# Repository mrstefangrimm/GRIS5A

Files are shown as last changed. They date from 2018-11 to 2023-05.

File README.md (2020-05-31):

# Marker Motion X-Ray Imaging Phantom
GRIS5A (working title) is a motion phantom with 5 motion axes which are controlled independently for both linear and rotary motion.
The name "Gris" "5A" comes from its color (gray) and the 5 axes. 

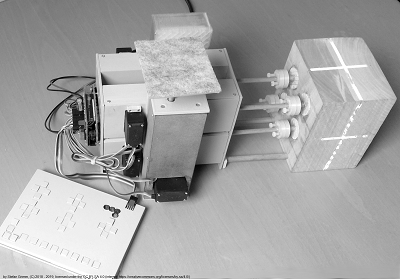
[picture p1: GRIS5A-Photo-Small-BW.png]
No2 Motion Phantom


## Project History
The project was launched in 2017 and has been added to github in 2018. In 2020, the software that is shared with other projects has been moved to its own repository named Phaso.

## Construction

A detailed description how to build this phantom is published on *[Instructables.com](https://www.instructables.com/id/Marker-Motion-X-Ray-Imaging-Phantom/)*.

## Manufacturing Tool Chain

### Mechanical Design

Tool | License 
---- | -------
SketchUp | SketchUp Shop 
Ultimaker Cura | GPL

### Hardware Design

Tool | License 
---- | -------
Fritzing | GPL

## License



This work is licensed under the Creative Commons Attribution-ShareAlike 4.0 International License. To view a copy of this license, visit http://creativecommons.org/licenses/by-sa/4.0/ or send a letter to Creative Commons, PO Box 1866, Mountain View, CA 94042, USA.

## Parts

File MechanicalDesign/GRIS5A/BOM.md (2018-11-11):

Anz. | Beschreibung
---- | ------------ 
2 | Holz Rundprofil d8 x 175
16 | M2 x 10 Universal Senkkopfschrauben mit S-Spitze
4 | M2 x 16 Universal Senkkopfschrauben mit S-Spitze
3 | LnR Actuator in linker Ausführung
2 | LnR Actuator in rechter Ausführung
1 | DKb Platine bestückt
1 | 8 pin Kabel
2 | 8 pin Stecker
1 | DKb-Front
1 | DKb-Back
1 | Niederstromnetzteil 230V/12V 0.7 A
1 | Niederstromnetzteil 230V/5V 2 A
1 | Stromkabel 2 phasig d0.4 x 200 für das Servoshield
1 | Stromkabel 2 phasig d0.4 x 200 mit Stecker d5.5/2.1 für den Arudino
1 | Stromkabel 2 phasig für den 230V Anschluss
1 | Gris5A-NetzteilGrundplatte
1 | Gris5A-NetzteilDeckel
1 | Arduino Uno R3
1 | Adafruit Servoshield PWM16
1 | Gris5A-Front
1 | Gris5A-Back
4 | Gris5A-Flansch
4 | Gris5A-FlanschHalter
2 | Gris5A-PhantomKlammer
1 | Gris5A-GatingGrundplatte
1 | Gris5A-GatingPlattform
1 | Gris5A-GatingBodenplatte
1 | Gris5A-GatingDeckplatte

<br />This work is licensed under a <a rel="license" href="http://creativecommons.org/licenses/by-sa/4.0/">Creative Commons Attribution-ShareAlike 4.0 International License</a>.

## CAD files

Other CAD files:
MechanicalDesign/Common/SketchUp/Cmn-Flange.skp
MechanicalDesign/Common/SketchUp/Cmn-FlangeClip.skp
MechanicalDesign/Common/SketchUp/Cmn-FrontClip.skp
MechanicalDesign/Common/SketchUp/Cmn-GatingPlatform.skp
MechanicalDesign/GRIS5A/SketchUp/DKb-Back.skp
MechanicalDesign/GRIS5A/SketchUp/DKb-Front.skp
MechanicalDesign/GRIS5A/SketchUp/Gris5A-Body.skp
MechanicalDesign/GRIS5A/SketchUp/Gris5A-BodyExplosion.skp
MechanicalDesign/GRIS5A/SketchUp/Gris5A-BodyRigidMarkers.skp
MechanicalDesign/GRIS5A/SketchUp/Gris5A-CylindersExplosion.skp
MechanicalDesign/GRIS5A/SketchUp/Gris5A-Flansch.skp
MechanicalDesign/GRIS5A/SketchUp/Gris5A-FlanschHalter.skp
MechanicalDesign/GRIS5A/SketchUp/Gris5A-FrontPlatte.skp
MechanicalDesign/GRIS5A/SketchUp/Gris5A-GatingBodenplatte.skp
MechanicalDesign/GRIS5A/SketchUp/Gris5A-GatingDeckplatte.skp
MechanicalDesign/GRIS5A/SketchUp/Gris5A-GatingGrundplatte.skp
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

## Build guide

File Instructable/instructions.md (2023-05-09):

# Marker Motion X-Ray Imaging Phantom

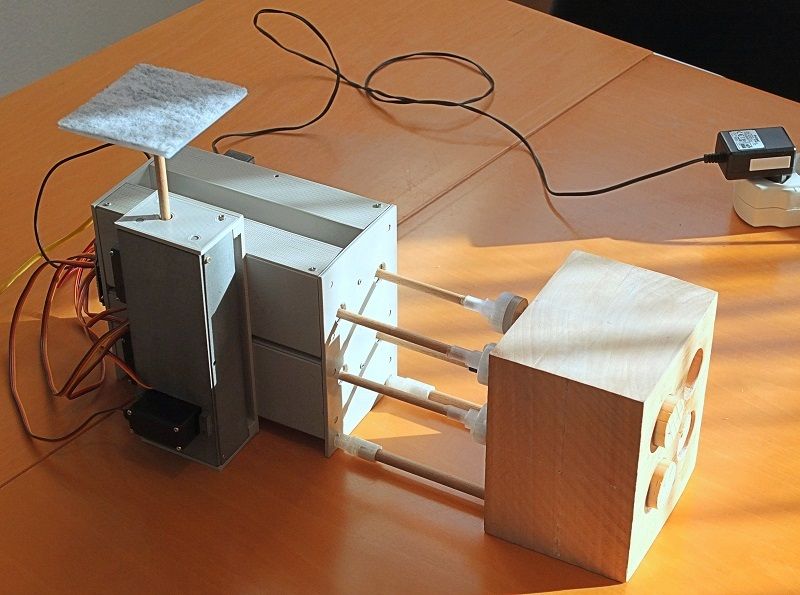
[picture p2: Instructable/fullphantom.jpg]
fullphantom


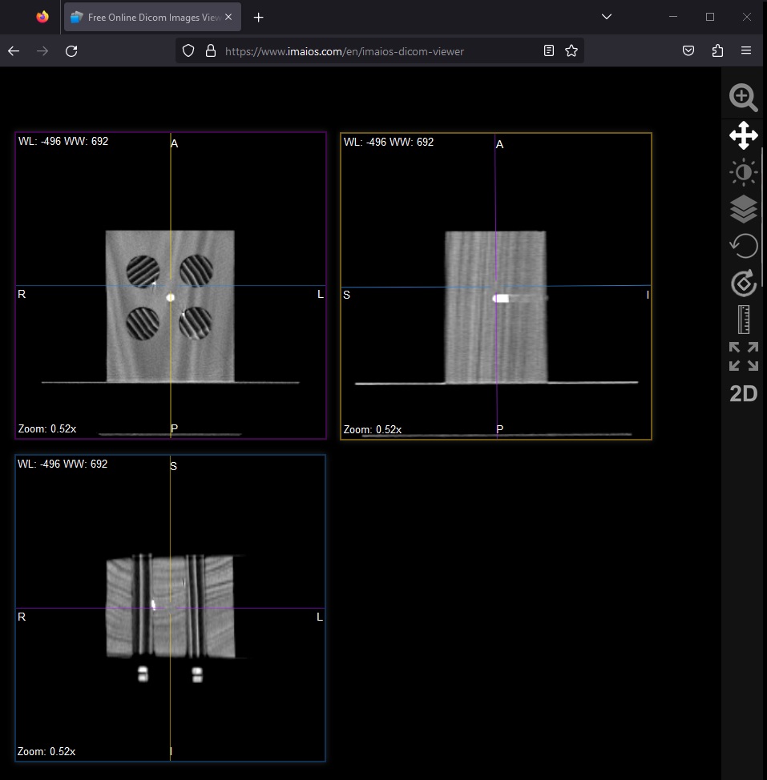
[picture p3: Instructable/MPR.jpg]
MPR


https://youtu.be/TMkLDR-dig4
https://youtu.be/PLr7lDx5VoA
https://youtu.be/z_6X1krTg_E

In the field of medical imaging, so called imaging phantoms are used  to evaluate, analyze, and tune the performance of various imaging  devices (Source: Wikipedia). 

Markers, or fiducial markers, are small, highly visible objects implanted in the patient’s body and used as “landmarks”.  Markers are implanted in  organs like the liver, the prostate, the pancreas or even the lung.  Markers in medical imaging are used to correlate images or to track  motion. This specially developed imaging  phantom simulates marker motion based on respiratory motion.

The idea for this phantom came when I studied marker motion. In a prostate, markers are implanted to correlate images. The markers do  not move during the image acquisition unless the patient moves. It is  possible that the markers slowly move over days which leads to different topologies. Markers in a liver move up and down with the respiratory  motion. Markers in the liver move as a group whereas in the lung, marker may move in different directions when the patient breathes.

On an X-Ray image, the material and the density define what is a  bone, a liver or a lung. Wood for example is similar to a lung. The four freely movable cylinders are made of wood and are used to simulate motion of the markers. The metal markers have a much higher density (> 10000 times higher) than wood and are clearly visible on an X-Ray image.

This short animation demonstrates some motion patterns of the Marker Motion X-Ray Imaging Phantom in simulation and reality:
https://youtu.be/S2i1PQueZQw

To generate the motion, the phantom uses five [LnR-Actuators](https://www.instructables.com/id/Linear-and-Rotation-Actuator/), an Arduino micro controller and an Adafruit Servo Shield. The phantom can be remote controlled from a Windows PC or Android Device over an USB cable.

This phantom is suitable to evaluate and tune the performance of medical devices. A field of application could be the development of motion tracking and marker detection and matching algorithms. With the used materials, imaging dosimetry is not possible. 

The direct material costs are approximately USD 250.

### Supplies:

1 Arduino Uno

1 Adafruit 16-Channel Servo Shield

5 [LnR-Actuator](https://www.instructables.com/id/Linear-and-Rotation-Actuator/)

4 Metal marker d1 x l4 mm, created from paper clip

9 Screw M2 x l10

4 Screw M2 x l20

1 Wooden block l100 x w120 x h180 mm

4 Wooden cylinders  d30 x l100 mm

4 Wooden dowel d6 x l25 mm

1 Wooden dowel d6 x l42 mm

2 Wooden dowel d8 x l166 mm

2 Wooden dowel d8 x l110 mm

3 Graphite lead of a pencil d2 x l12 mm

8 Graphite lead of a pencil d2 x l5 mm

1 Windows PC with Java 8 runtime and .NET Framework 4.6.2

1 3D Printer

1 Standing drill and drills for wood: d30, d8, d6 and d2 mm

Legend: l:length, d:diameter, w: width, h:height

## Step 1: 3D Printed Parts

PLA, default 20% infill: Cmn-FlangeClip.stl, Cmn-FrontClip.stl, Cmn-GatingPlatform.stl, MMXIP-Back.stl, MMXIP-Flange.stl, MMXIP-FlangeCylinder.stl, MMXIP-Front.stl, MMXIP-GatingBase.stl, MMXIP-GatingBottom.stl, MMXIP-GatingTop.stl

## Step 2: Build the Phantom Body

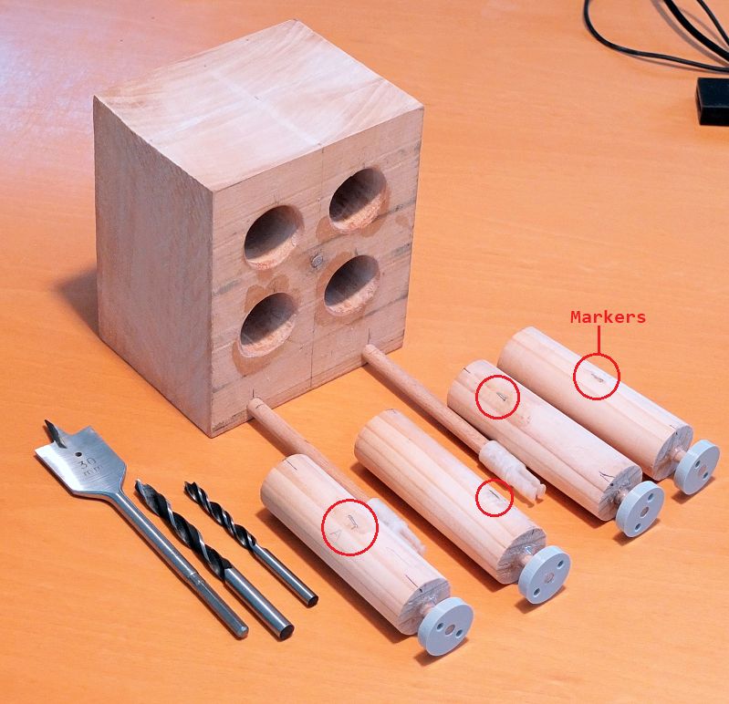
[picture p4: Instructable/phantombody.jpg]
phantombody

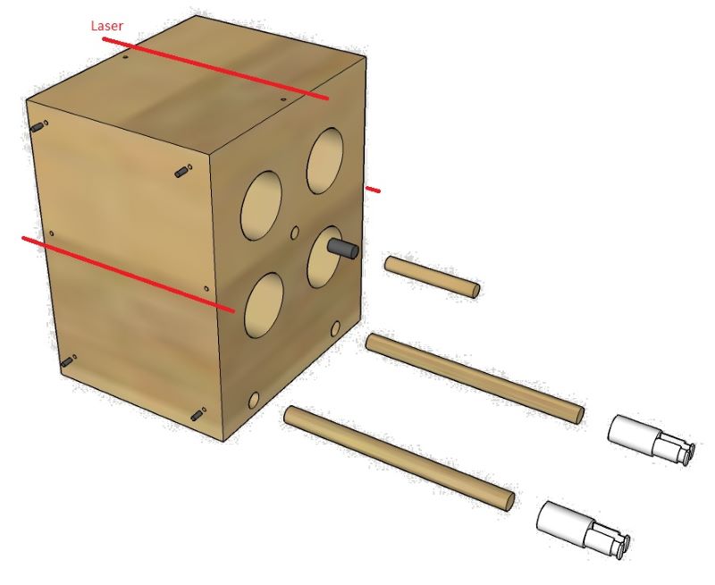
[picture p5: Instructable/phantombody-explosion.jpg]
phantombody

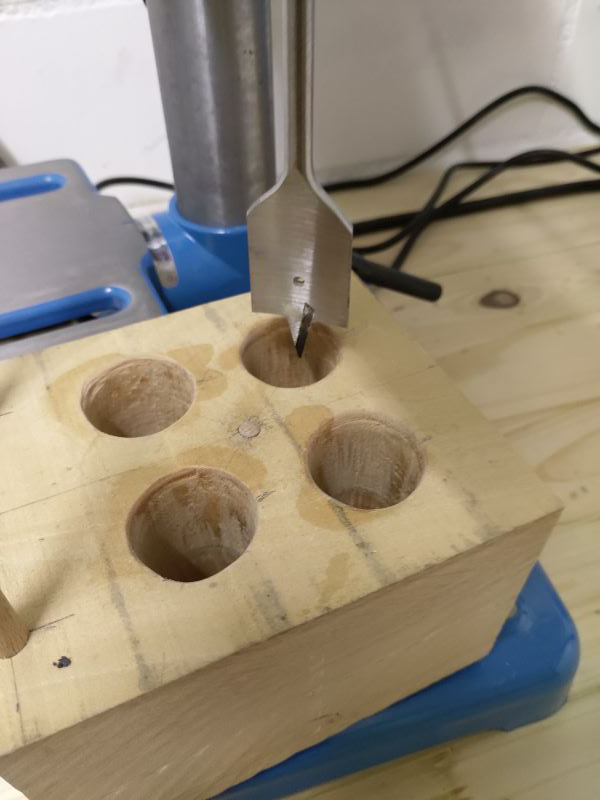
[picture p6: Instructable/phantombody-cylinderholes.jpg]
phantombody

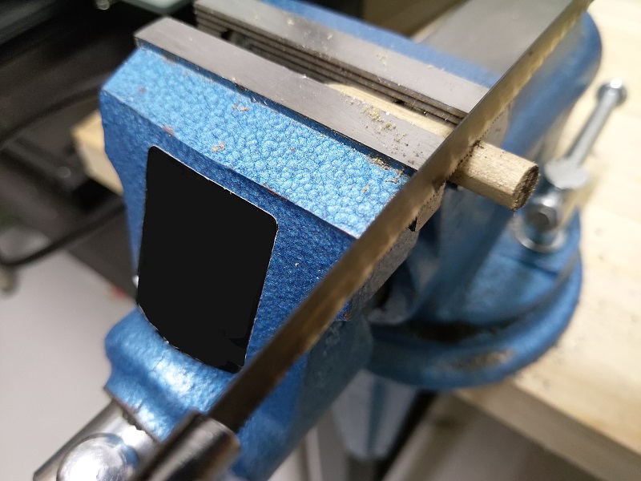
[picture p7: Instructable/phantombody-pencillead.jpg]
phantombody

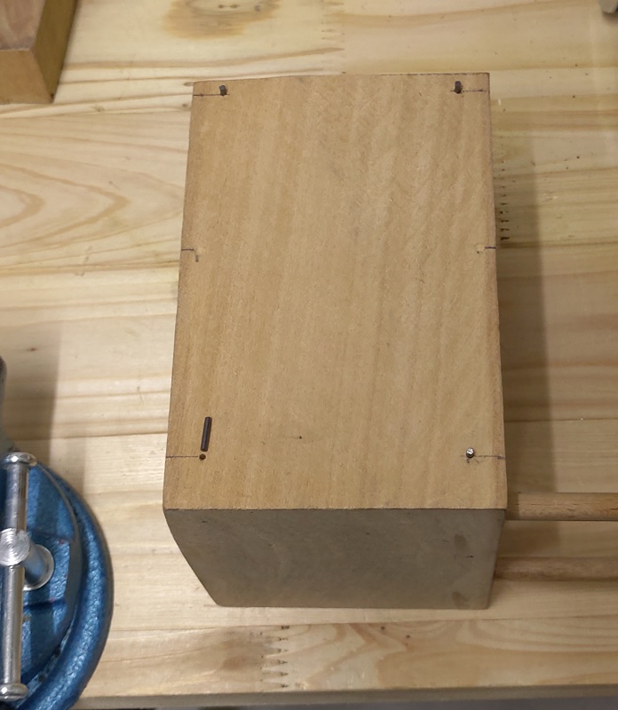
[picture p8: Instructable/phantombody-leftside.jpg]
phantombody


The "phantom body" is the wooden cube as seen in the images above. It has 4 bores that allow the cylinders to rotate and move back and forth. In the center of the four cylinder bores is a 6 mm hole filled with graphite from a pencil lead (this is clearly visible on an x-ray and represents the target).

Markings on the sides and top of the phantom help align the phantom with the laser. On the left and right side are four pins made from a pencil lead as rigid markers visible on x-rays.

First, use a pencil to mark where you need to drill. The center of the 4 cylinder bores is at a height of 79 mm. the distance from cylinder to cylinder bore is 50 mm. The holes for the distance holders are at a height of 8 mm and the distance between them is 70 mm.

The depth of the center hole is 54 mm. It is filled with 12 mm  graphite closed with a wooden rod (42 mm). The depth for the 2 holes for the distance holders is 10 mm.

It is up to you where and if you want to add the graphite pins on the left and right side. However, the markings for the lasers should be on the same height as the target.

## Step 3: Assemble the four Cylinders

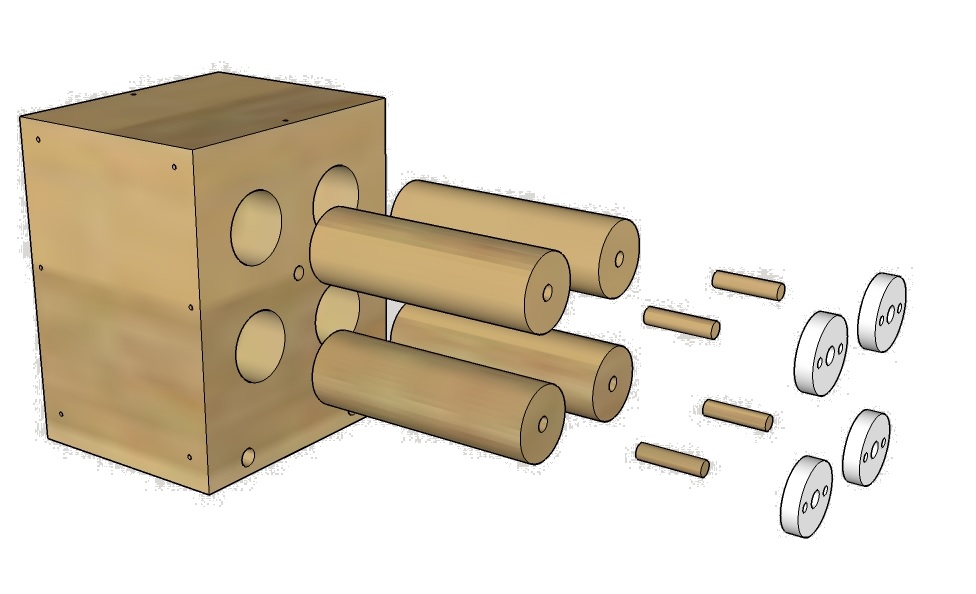
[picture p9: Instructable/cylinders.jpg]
cylinders


Cut a M4 thread into the two d3.3 mm holes in the *MMXIP-Flange*. Bore a hole of d6 x 6 mm diameter into the front of the cylinder. Insert a dowel d6 x 25 mm and add a *MMXIP-Flange*. Fixate it with some glue.

To add the markers at the correct, position, insert the cylinders into the phantom body and align the cylinders such that the flanges are horizontally. On each cylinder, make a mark with a pencil towards the center of the phantom and add the metal markers as shown on the picture in the step above.

## Step 4: Assemble the Actuator

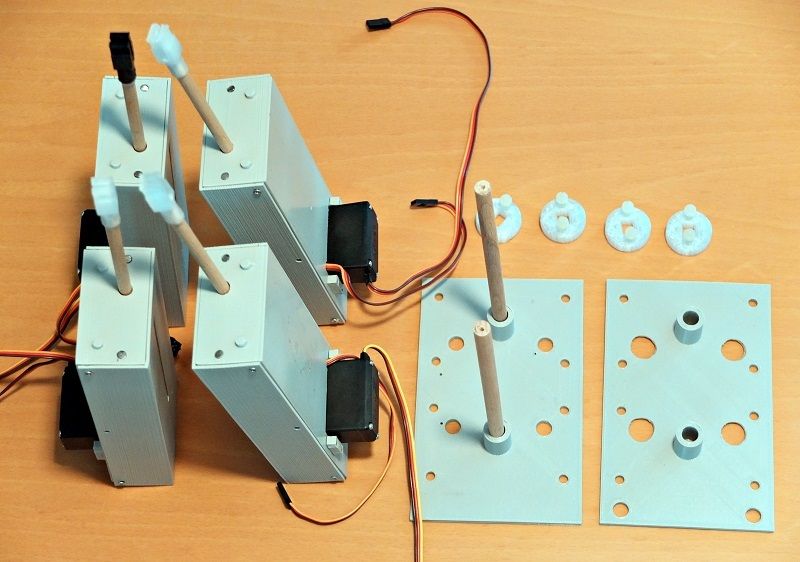
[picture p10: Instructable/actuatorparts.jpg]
actuatorparts


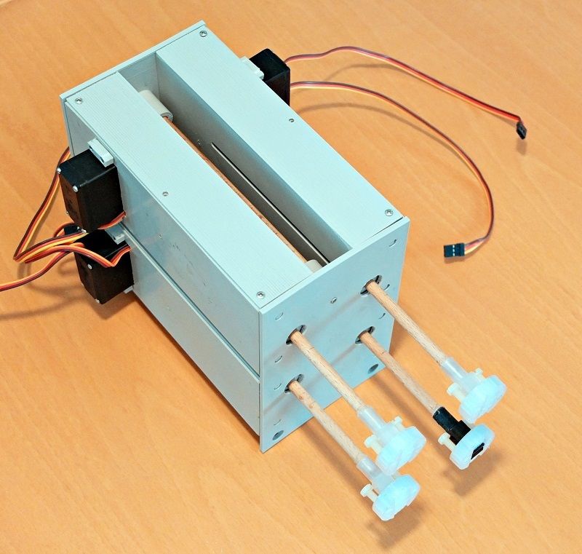
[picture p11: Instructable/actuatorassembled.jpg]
actuatorassembled


To build the actuator assembly, fixate two wooden dowels d8 x l166 mm to the *MMXIP-Back* with two screws M2 x l20 mm. Plug-in the four LnR-Actuators and add the *MMXIP-Front*. Add a *Cmn-FlangeClip* to each of the LnR-Actuator shafts but do not fixate it yet.

Plug-in the assembled phantom body into the actuator assembly. First screw the *MMXIP-Flange* to the cylinders and use plastic screws M4 x l20 mm to fixated it. Connect the flange-clip with the flange. Align the cylinders and then fixate the flange clips with some glue to the actuator shafts.

## Step 5: Add the Gating Platform

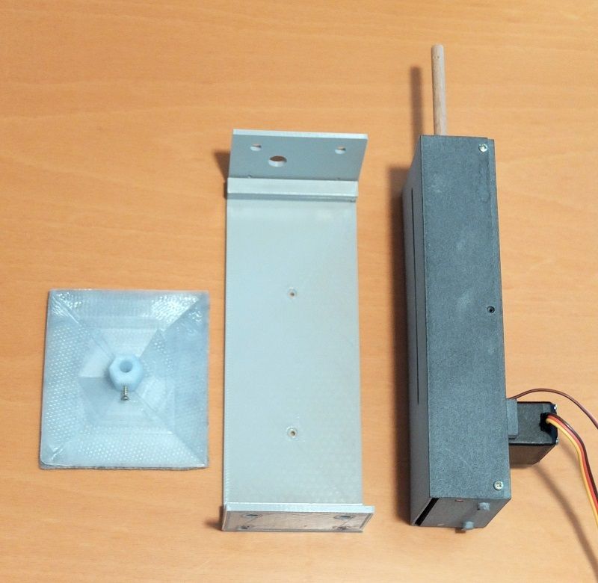
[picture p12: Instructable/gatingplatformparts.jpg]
gatingplatformparts


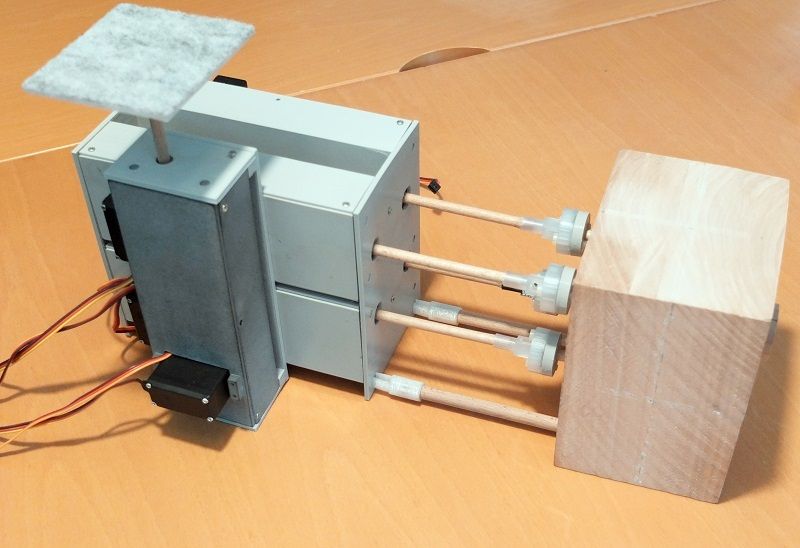
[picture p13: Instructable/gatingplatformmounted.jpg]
gatingplatformmounted


To build the Gating assembly, add the *MMXIP-GatingBottom* and the *MMXIP-GatingTop* to the *MMXIP-GatingBase* with screws M2 x l10 mm and add it the the actuator assembly with two screws M2 x l10 mm. Add the *Cmn-GatingPlatform* and fixate it with a screw M2 x l10 mm.

## Step 6: Add the Micro Controller

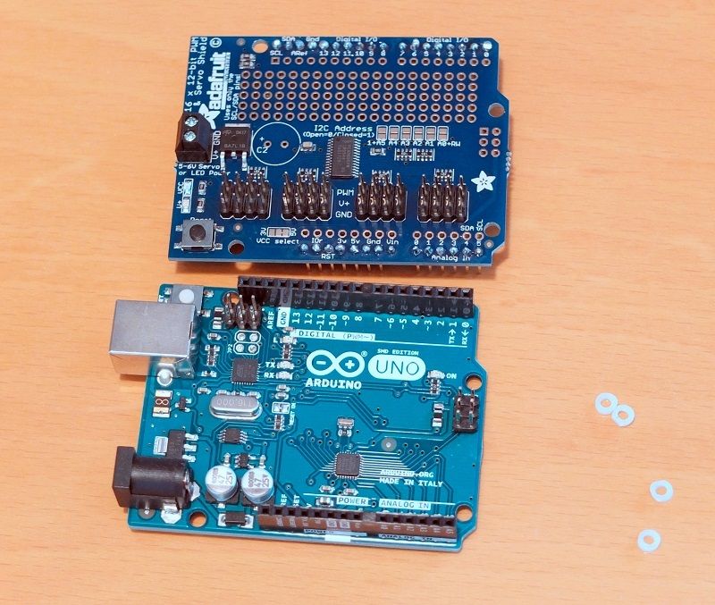
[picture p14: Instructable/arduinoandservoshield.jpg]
arduinoandservoshield


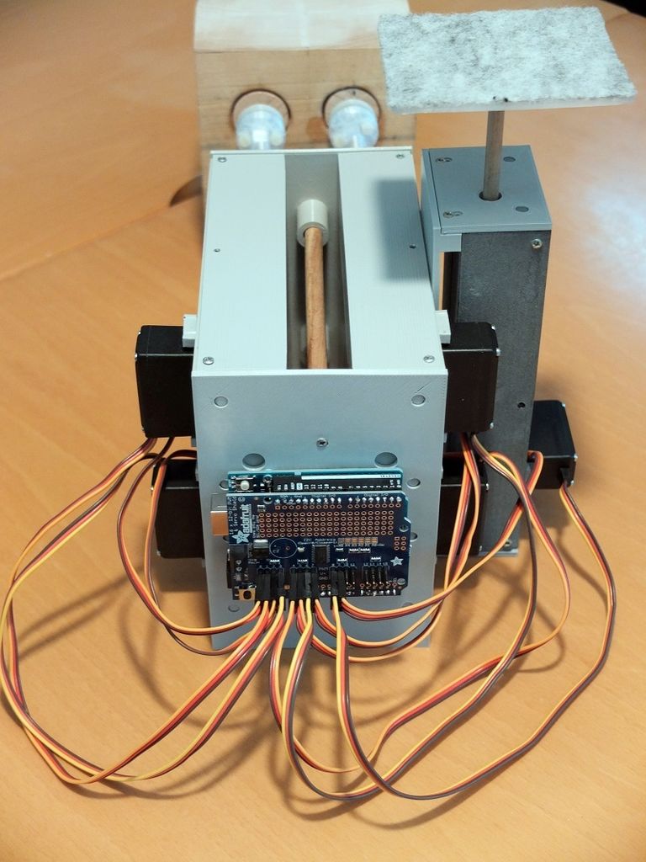
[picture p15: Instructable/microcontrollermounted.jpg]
microcontrollermounted


Use four distance rings to prevent the micro controller board  from touching the back panel. Fixate the Arduino with four screws M2 x l10 mm on the *MMXIP-Back* and attach the Adafruit Servo Shield.

Connect the servos to the servo  shield in this order: Rotary (short cable) Lower, Upper, Gating. Longitudinal (long cable) Lower, Upper, Gating.

Connect the servos to the servo  shield in this order: LUR, LUL, LLR, LLL, RLL,  RLR, RUL, RUR, GAL, GAR.

LUR: Left Upper Rotary servo motor, LUL: Left Upper Longitudinal, LLR: Left Lower Rotary, ...,  RLL: Right Lower Longitudinal, GAL: GAting Longitudinal, ...

## Step 7: Install the Firmware and Calibrate

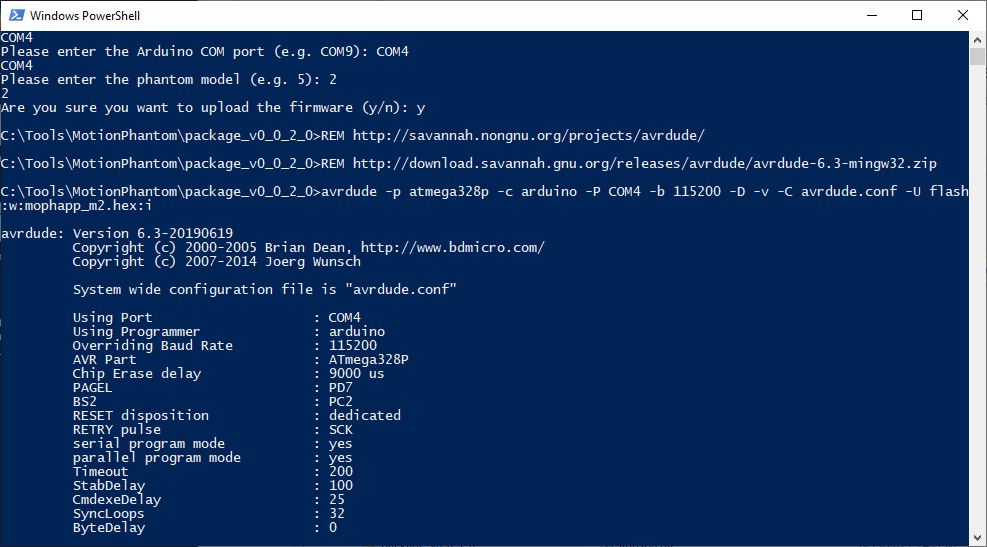
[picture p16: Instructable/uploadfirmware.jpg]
uploadfirmware


Download the package.zip (e.g. package_v0.0.2.0.zip) of the latest release from [github](https://github.com/mrstefangrimm/Phaso/releases/). The download includes the required scripts and the software to control the phantom. Unzip the package into a local folder, e.g. C:\Tools\MotionPhantom. 

Connect the phantom to your PC before the next steps.

In the download is a PowerShell script that uploads the firmware and write the calibration data to the EEPROM. To execute the script, open a PowerShell and change the directory to the target folder and then run: .\setup.ps1. Or right-click on the setup.ps1 and select Run with PowerShell.

- The script now lists one or more COM ports. Enter the phantom's port (e.g. COM13).

- For the model, enter: 3

- Confirm the firmware upload with: y

  The script uses avrdude to upload the firmware. After the upload, the firmware is active.

- Confirm the EEPROM update with: y

  The script writes the default calibration to the EEPROM.

- Confirm to run a test with: y

  The test ends with the output: Complete, and resets the firmware.

The phantom is ready for use.

## Step 8: Remote Control It With the Virtual Phantom Application

https://youtu.be/4L0OvpXcFAo

The Virtual Phantom Application is a .NET based application and part of the downloaded package (\Virms.NET\ViphApp.exe). The application simulates X-Ray imaging. And it is possible to connect and control a phantom with the application.

When you start the program, the Marker Phantom is already selected.

If the phantom is plugged-in, its port should in the list. Select the port and press "Connect".

On the right control panel, it is possible to either control the motion axes individually or start a program.

If you plan to write your on software: This programming interface is completely documented in this [Wiki](https://github.com/mrstefangrimm/Phaso/wiki).

## Step 9: Control It From Your Phone

https://youtu.be/MwSjcJiLyaM

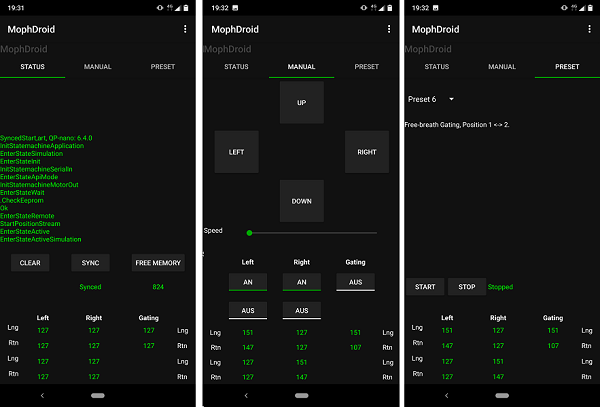
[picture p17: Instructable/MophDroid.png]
mophdroid


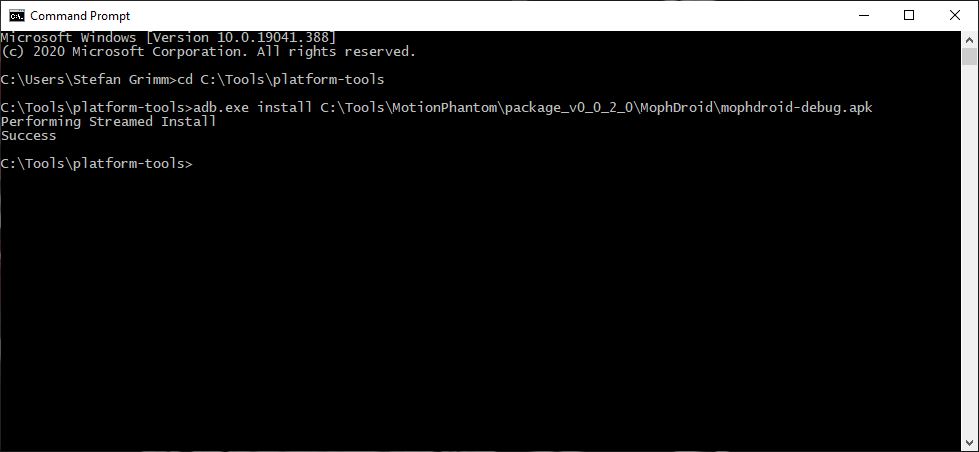
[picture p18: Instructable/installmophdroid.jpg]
[installmophdroid]()


MophDroid is a Android App that allows you to control the phantom from your phone. This App replaces the need to every time wire your PC to the phantom. Instead you may install the App on a discarded smartphone which you then leave connected to the phantom. Like this, the phantom is always ready for use.

To install the App you have to enable the developer options on your phone. Follow [these instructions](https://www.xda-developers.com/install-adb-windows-macos-linux/) to setup your phone and your PC.

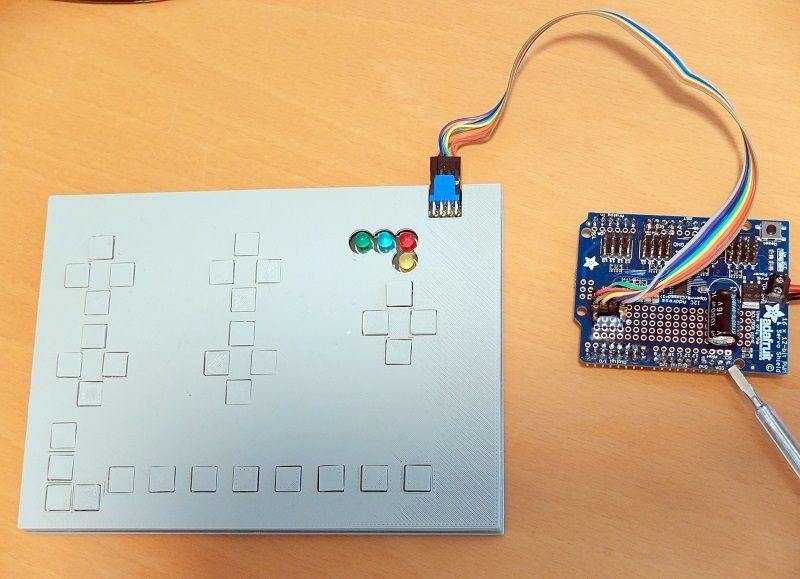
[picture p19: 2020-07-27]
Instructable/DKb.jpg

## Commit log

2018-05-22 Some files
    [Print1-PLA-Once.skp, Print2-PLA-Twice.skp, Print3-PLA-Twice.skp]
2018-05-24 Renamed LaR to LnR
    [Print1-PLA-Once.skp, Print2-PLA-Twice.skp, Print3-PLA-Twice.skp]
2018-06-06 Added Software/SoftDKb and Software/calibration
2018-06-07 Added DKb (HW)
    [GRIS5A-DKb-r1.fzz]
2018-06-07 Increase hole size on the PCB to 0.9 mm everywhere
    [GRIS5A-DKb-r1.fzz, GRIS5A-DKb.fzz]
2018-06-07 Changed LED color for playback mode to yellow
2018-06-13 Moved content under "Mechanics"
    [Print1-PLA-Once.skp, Print2-PLA-Twice.skp, Print3-PLA-Twice.skp]
2018-06-20 Added SketchUp models for DKb and GRIS5A front and back panel
    [Print1-PLA-Once.skp, Print2-PLA-Once.skp]
2018-06-20 Minor changes on the DKb layout
    [GRIS5A-DKb.fzz]
2018-06-23 Changed ServoShieldPCA9685Linear.write() method
2018-06-23 Fixed key mapping in calibration application
2018-06-25 Remove holes from backplane
    [Print2-PLA-Once.skp]
2018-06-26 More Sketchup models to print
    [Print3-PLA-Once.skp]
2018-07-06 Fixed holes in ground and top plate for the Gating mount.
    [Print3-PLA-Once.skp]
2018-07-28 Increased height of the DKB front. Added new motion phantom sketch and photo with the actual size of the gating platform and the power supply.
2018-07-28 Increased DKB front height by 0.8 mm.
    [Print1-PLA-Once.skp]
2018-08-09 Updated polyominal for LLLNG because the motor was replaced
2018-08-09 Added copyright notice to SketchUp print models
    [Print1-PLA-Once.skp, Print2-PLA-Once.skp, Print3-PLA-Once.skp]
2018-08-22 Added SketchUp models and BOM for the LnR-Actuator.
    [LnR-ChassisHaube-PLA.skp, LnR-ChassisHaube.skp, LnR-ChassisLinks-PLA.skp, LnR-ChassisLinks.skp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]
2018-08-22 Added missing LnR Actuator SketchUp model
    [LnR-Flansch-Kreuz.skp]
2018-08-25 Added SketchUp models for the Gris5A phantom and BOM for it.
    [DKb-Back.skp, DKb-Front.skp, Gris5A-Back.skp, Gris5A-Flansch.skp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]
2018-11-11 Removed obsolte line from a sketchup model.
    [Gris5A-Front.skp]
2018-11-24 Decrease motor update interval 100 to 40ms and DBK read interval form 200 to 100ms, Updated the PreSet programs due to the new timing. Removed several "Serial.println" which are no longer possible wi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
2018-11-25 Changed initialization of the motors by initializing one by one with a delay of 200 ms in between. Startup problems due to a too high voltage drop should be solved by that.
2018-12-11 Adapted calibration applicaiton to the new serial-in commands
2018-12-29 Updated calibration data for all motors. Commented out "Serial.printlns".
2019-01-25 Removed the LnR-Actuator. It has now its own repository.
    [LnR-ChassisHaube-PLA.skp, LnR-ChassisHaube.skp, LnR-ChassisLinks-PLA.skp, LnR-ChassisLinks.skp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]
2019-03-18 Upgraded to QM 4.4.0, QPN 6.4.0 for Arduino
2019-05-01 Added frontclip SketchUp model.
    [Gris5A-FrontClip.skp]
2019-05-05 Changed state machines. Uses 1 application state machine. the obsolete state machines still have to be removed. Included the calibration application into the application state machine.
2019-05-19 Changed from prfServo to prfServo2, without calibrating though. Bug fixed for phantom No2.
2019-05-23 Fixed sending of motor positions for number of servos other than ten.
2019-05-25 Changed serial out messages to support 16 servos. Changed the messages for state changes (manual, preset, remote and calibration) from A-E to G-K.
2019-05-27 Renamed Arduino program gris5A mophapp and gris5alib mophlib.
2019-05-27 Removed generated Arduino files from the git repository.
2019-08-03 Change calibration initial position to150.
2019-08-03 Add PROGRAM_CHANGE (change of speed in this context) trigger to the Calibration state.
2020-02-16 Squashed commit of the following:
    commit 31a51df57757fdd216396cbb978448d90852a41e
    Author: mrstefangrimm <motionsystems@grimm.com>
    Date: Sun Feb 16 22:36:56 2020 +0100
    Add Instructable dir.
    commit d3d058a1c62a958f84344d34c0e87b961d35a182
    Author: mrstefangrimm <motionsystems@grimm.com>
    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
    [Gris5A-Back.skp, Gris5A-ZylinderFlansch.skp]
2020-02-22 Revert "Delete osolete files."
    This reverts commit a35df43383a62782c72923777e768092c0dc4602.
    [Gris5A-Back.skp, Gris5A-Front.skp, Gris5A-NetzteilDeckel.skp, Gris5A-NetzteilGrundplatte.skp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]
2020-02-22 Replace binaries with generated binaries from Trimble.
    [DKb-Back.skp, DKb-Front.skp, Gris5A-Flansch.skp, Gris5A-FlanschHalter.skp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]
2020-02-22 Replace and rename binary.
    [Gris5A-Back.skp, Gris5A-Rueckwand.skp]
2020-04-25 Moved Sketchup models FrontClip and GatingPlatform to Common and added Flange and FlangeClip to Common
    [Cmn-Flange.skp, Cmn-FlangeClip.skp, Cmn-FrontClip.skp, Cmn-GatingPlatform.skp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]
2020-05-18 Update Sketchup models
    [Cmn-Flange.skp, Cmn-FlangeClip.skp, Cmn-FrontClip.skp, Cmn-GatingPlatform.skp]
2020-05-24 Redesign. moved functions into device specific files.
2023-05-01 Add rigid markers and target to Sketchup models. Update instructions.
    [Gris5A-Body.skp, Gris5A-BodyExplosion.skp, Gris5A-BodyRigidMarkers.skp, Gris5A-CylindersExplosion.skp]
